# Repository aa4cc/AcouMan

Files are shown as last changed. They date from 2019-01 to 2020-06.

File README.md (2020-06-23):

# AcouMan - a platform for acoustic manipulation
[index](README.md)

# _!! IMPORTANT -- repository relocated !!_
Content in this repo is no longer updated.
Go to (https://gitlab.fel.cvut.cz/aa4cc/acouman/acouman-main) to get the latest version.
# _!! !!_

AcouMan is a platform for acoustic manipulation, that is for manipulating objects via shaping the surrounding acoustic pressure field. You can see the platform in the figure below and a detailed description will be (hopefully) published soon. If you want to see the platform in action, check our [video](https://youtu.be/BdDq_jRSNYA) showing some experiments with the platform.

This repository contains all files needed to reproduce the platform.

* [_MATLAB Optimization/_](MATLAB&#32;optimization/readme.md) folder contains Matlab scripts implementing a solver of the optimization problem where one looks for such phase shifts of the signals driving the transducer array that a given pressure point in space is generated
* [_FPGA generator/_](FPGA_generator/readme.md) folder contains a Quartus project for the 64 channel generator
* [_calibration/_](calibration/readme.md) folder contains all scripts for calibrating the camera
* [_manufacturing/_](manufacturing/readme.md) folder contains all drawings for a laser cutter, 3D models and PCB designs for manufacturing the platform
* [_simulink/_](simulink/readme.md) folder contains Simulink schemes for controlling the platform in various modes
* [_visualization/_](visualization/readme.md) folder contains Matlab scripts for visualization of the generated pressure field by the transducer array driven by square waves with specified phase-shifts
* [_webinterface/_](webinterface/readme.md) folder contains Python scripts for the web interface running on the Raspberry Pi

## Building the platform

If you want to build the platform, please refer to the guides on [mechanical assembly](docs/assembly.md) and [software](docs/software.md).

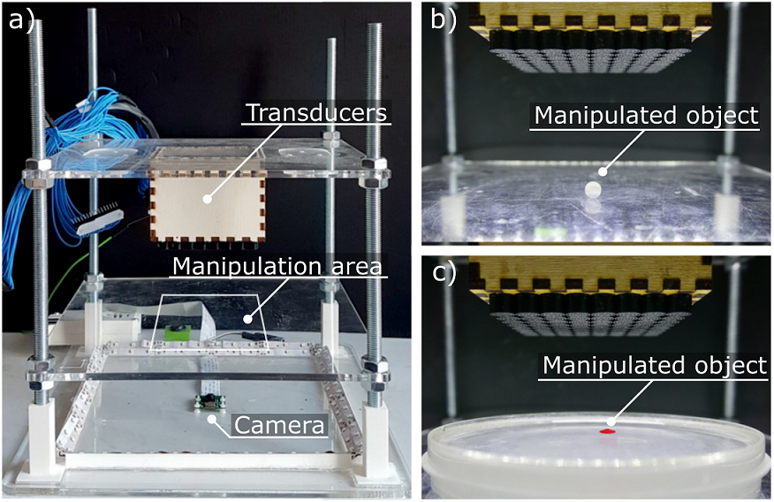
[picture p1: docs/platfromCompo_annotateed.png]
Photos of the platform


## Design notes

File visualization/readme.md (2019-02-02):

# Acoustic pressure field visualization tools
[index](../README.md) \> [visualization](readme.md)

Use the 'acousticPressureSlice' GUI to visualize the acoustic pressure field generated by the transducers. The GUI allows you to load the phase delays, either from the MATLAB workspace or a .mat file. You can set different slice planes (currently, only planes perpendicular to axes, ie. x = c, y = c or z = c, where c is an arbitrary constant, are supported). You can set the limits of the axes and resolution.

Alternatively, you can use the 'acousticPressure3D' function to calculate the pressure field, and then use function like 'slice' or 'isosurface' to visualize the field. To visualize the phase delays of the transducers, use the 'plotPhases' function.

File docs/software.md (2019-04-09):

# Building the platform - software
[index](../README.md) > [software](software.md)

For rapid prototyping, we use the following strategy:
We create our control scheme in MATLAB/Simulink and then deploy it to the Raspberry Pi.
The Raspberry then runs the control algorithm, which accepts the reference setpoints remotely via UDP.
This allows us to control the platform from a simple web interface.

## Configuring your PC

### Requirements

In order to deploy the controller to Raspberry Pi, you will need MATLAB & Simulink R2018b or newer _(note: we use this version of MATLAB, because it supports Raspberry Pi 3B+)_ with the following toolboxes/packages:
 * Simulink coder
 * Control systems toolbox
 * Simulink support package for Raspberry Pi

Also, your computer must have an SD card reader.

### Starting the Simulink models

If you change your working directory to _simulink_ and open any of the models, the startup functions should automatically add all necessary folders to MATLAB path.
If you encounter an error, try to run the scripts `BOD_startup` and `BOW_startup` manually.

## Configure the Raspberry Pi

### Install Raspbian with MATLAB server

Insert an empty microSD card in your computer.
In MATLAB, go to the _HOME_ card and select _Add-Ons-\>Manage Add-Ons_.
An Add-On Manager window should appear.

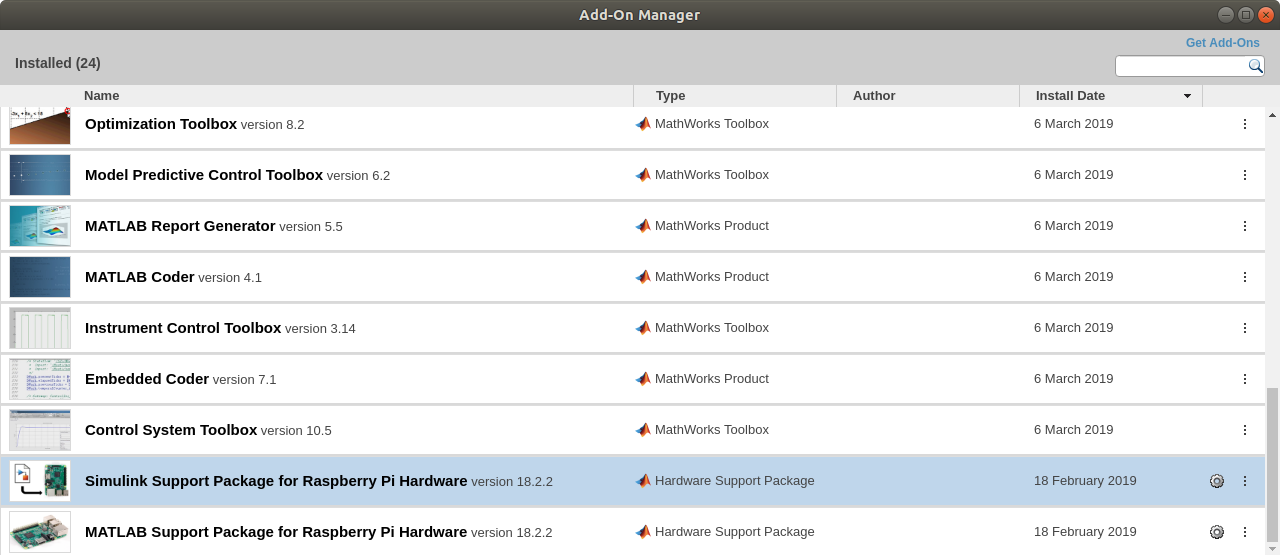
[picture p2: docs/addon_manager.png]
Add-On Manager


Find the Simulink Support Package and click on the Setup button (the gear).
Follow the guide and install the Raspbian image.

### Copy necessary files

From this repository, you will only need folders `raspi-ballpos` and `webinterface`.
On UNIX systems, use the following command to copy them from your computer:
```
scp -r raspi-ballpos/ webinterface/ pi@xxx.xxx.xxx.xxx:~
```

### Enable Camera

Either directly in the Raspberry Pi terminal, or remotely via SSH, type:
```
sudo raspi-config
```
and select the `Enable Camera` option.

### Install dependencies

#### OpenCV

Follow [this guide](https://www.pyimagesearch.com/2016/04/18/install-guide-raspberry-pi-3-raspbian-jessie-opencv-3/) on installing OpenCV on Raspbian Jessie.
_Note: The installation is quite lenghty. If you do it remotely, we recommend using `screen`, so you can disconnect without interrupting the process_

#### C++ libraries

Download [Eigen](http://eigen.tuxfamily.org/) and [LBFGS++](http://yixuan.cos.name/LBFGSpp/) libraries, and copy them to `/usr/include/`.

#### Python modules

Install the following modules using `pip`:
``` 
sudo pip3 install picamera click flask flask_socketio matplotlib profilehooks RPi.GPIO screeninfo imutils eventlet requests scipy
```
In addition, it may be necessary to upgrade the numpy module provided during OpenCV installation:
```
sudo pip3 install numpy --upgrade
```
Also, there are two custom packages in the `raspi-ballpos` folder that must be installed:
```
cd raspi-ballpos
cd sharemem/
sudo ./install
cd ../find_object/
sudo ./install
```

### Services

Copy all service files from `webinterface`:
```
sudo cp ~/webinterface/*.service /lib/systemd/system/
```
Enable the services at startup:
```
sudo systemctl enable posmeas.service 
sudo systemctl enable ultraman.service
sudo systemctl enable ultraman_web.service
```

### Configuration files

Move the configuration files from `webinterface` to user folder:
```
mv ~/webinterface/*.json ~/
```

## Deploy the controller

Open the Simulink model `simulink/allInOne.slx`.
Go to the _Model Parameters_ (the gear icon) and select _Hardware Implementation_.
Set _Hardware Board_ to Raspberry Pi, expand the _Target Hardware Resources_ tab and fill in the _Board Parameters_, as shown in the picture.

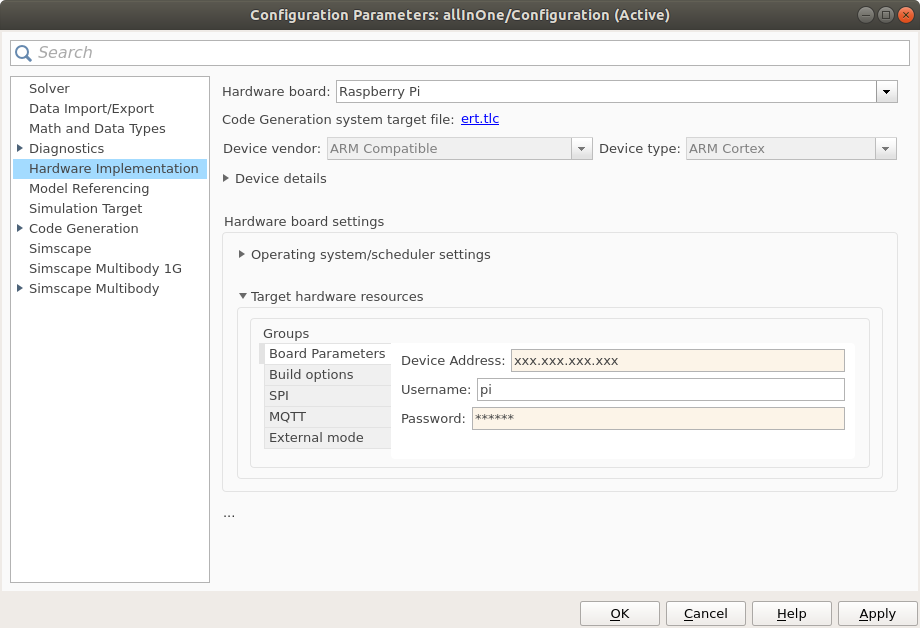
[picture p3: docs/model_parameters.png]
Model Parameters


Go to the _Build Options_ group and select _Build_ as the _Build Action_. Set the _Build Directory_ to `/home/pi`.

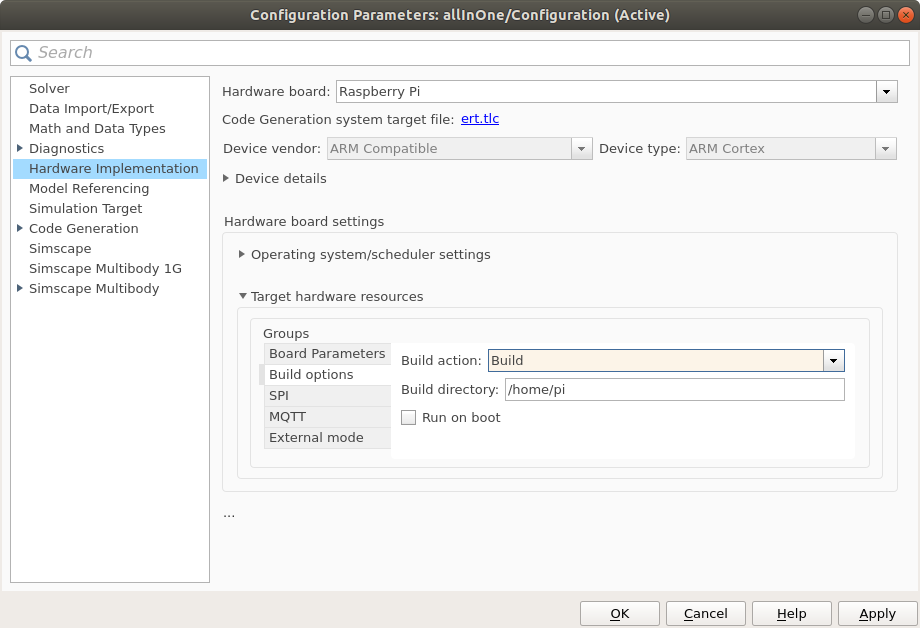
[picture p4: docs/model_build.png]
Model Parameters


Apply the changes and exit the _Model Parameters_ window.

Now, you can click on the _Deploy to Hardware_ button (the serial port icon).
If you cannot see the button, change the _Simulation Mode_ to _External_.

Since the R2018b version, MATLAB doesn't create the deployed model in the user folder.
You need to copy the controller:
```
cp ~/MATLAB_ws/R2018b/path_to_repository/simulink/allInOne.elf ~
```

## Controlling the platform

Now, you should be able to control the platform from the web interface.
Start the services so you don't need to restart the Raspberry.
```
sudo systemctl start posmeas.service 
sudo systemctl start ultraman.service
sudo systemctl start ultraman_web.service
```

On your computer, open a web browser.
The web interface should be accessible from port 5000 (`xxx.xxx.xxx.xxx:5000`).

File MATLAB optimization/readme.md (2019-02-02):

# MATLAB optimization scripts (deprecated)
[index](../README.md) \> [MATLAB optimization scripts](readme.md)

This document contains a brief introduction to the MATLAB optimization scripts. These scripts calculate phase delays for an array of 64 ultrasonic transducers. 

## Levitation

The 'levitation' folder contains scripts for single beam levitation method shown in an article by [Asier Marzo](https://www.nature.com/articles/ncomms9661). To generate the phase delays, run 'solverscript.m'. You must have the 'MATLAB optimization' folder in your MATLAB path to run this script. 

## Ghost Touch 

The 'ghostTouch' folder contains scripts for creating focused acoustic pressure, similarly to [Ghost Touch](http://doi.acm.org/10.1145/2817721.2817727). To generate the phase delays, use the function 'pressurePoints'. You must have the 'MATLAB optimization' folder in your MATLAB path to run this script.

__NOTE: All optimization scripts are now rewritten in C++ to be ran on the _Raspberry Pi_, the MATLAB scripts can still be used for verification.__

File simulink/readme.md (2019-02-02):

# Simulink models
[index](../README.md) \> [simulink](readme.md)

This document contains a description of the Simulink models and their usage.

## Simulink models

The models require the MATLAB system object from [raspi-ballpos](https://github.com/aa4cc/raspi-ballpos) to function. In addition, the compiler on the target device must have the [Eigen](http://eigen.tuxfamily.org/) and [LBFGS++](http://yixuan.cos.name/LBFGSpp/) libraries. All models are made to obtain reference or parameters via UDP. This can be done either using the simple MATLAB GUIs, or the Python [web interface](../webinterface/readme.md).

### All in one

This model implements all three models (bubbles, ball on solid surface, ball on water) with a switching system. It is created to be used with the [web interface](../webinterface/readme.md).

### Bubbles

This is a simple demonstration model. It creates a high-pressure point at a specified position.

### Ball on solid (dry) surface

This model implements a controller for positioning a ball on a dry surface. If the controller fails to stabilize the ball, check the calibration of the platform.

### Ball on water

This model implements a controller for positioning a floating ball. Ideally, the ball should be put in a transparent shallow container, such as a Petri dish, filled with water.

## GUIs 

The MATLAB GUIs are simple figures, set to appear on the secondary monitor. Check if the UDP port number in the .m files matches the UDP port number in the Simulink models.

All GUIs share similar controls. Dragging the circle changes position. In the 'bubbles' model, the mouse wheel changes the pressure intensity.

</html>

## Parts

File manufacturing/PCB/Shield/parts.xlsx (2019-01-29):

Parts needed for making 2 Shields
Farnell
Description | OC | Quantity | Unit price | Total
Cap. 1uF | 2494199 (https://cz.farnell.com/murata/gcm21br7ya105ka55l/cap-mlcc-x7r-1uf-35v-0805/dp/2494199) | 150 | 5.39 Kč | 808.95 Kč
Res. 0 Ohm | 2309112 (https://cz.farnell.com/multicomp/mc0805s8f0000t5e/res-thick-film-0r-1-0-125w-0805/dp/2309112) | 140 | 0.15 Kč | 20.86 Kč
Cap. 220uF | 2800123 (https://cz.farnell.com/teapo/ksh227m035s1g5h12k/cap-alu-elec-220uf-35v-rad/dp/2800123) | 6 | 3.31 Kč | 19.88 Kč
Cap. 100nF | 2896747 (https://cz.farnell.com/vishay/vj0805y104kxxac/cap-mlcc-x7r-0-1uf-25v-0805/dp/2896747) | 5 | 5.44 Kč | 27.22 Kč
Cap. 10nF | 2534062 (https://cz.farnell.com/wurth-elektronik/885012207066/cap-mlcc-x7r-0-01uf-25v-0805/dp/2534062) | 10 | 1.34 Kč | 13.38 Kč
Cap. 18pF | 2896683 (https://cz.farnell.com/vishay/vj0603a180jxbac/cap-mlcc-c0g-18pf-100v-0603/dp/2896683) | 10 | 3.67 Kč | 36.72 Kč
Cap. 4.7uF | 9451234 (https://cz.farnell.com/multicomp/mcgpr35v475m5x11/cap-alu-elec-4-7uf-35v-rad/dp/9451234) | 2 | 1.18 Kč | 2.36 Kč
Schottky | 2317416 (https://cz.farnell.com/on-semiconductor/nsr0320mw2t1g/diode-schottky-900ma-23v-sod-323/dp/2317416) | 5 | 5.01 Kč | 25.04 Kč
Polyfuse | 1861197 (https://cz.farnell.com/multicomp/mc36213/fuse-ptc-reset-smd-6v-500ma/dp/1861197) | 5 | 4.96 Kč | 24.78 Kč
Ferrite bead | 1301674 (https://cz.farnell.com/tdk/mmz2012y152b/ferrite-bead-0-4ohm-500ma-0805/dp/1301674) | 10 | 1.76 Kč | 17.64 Kč
LED - amber | 2251467 (https://cz.farnell.com/vishay/vlmk233u1aa-gs08/led-mini-amber-power/dp/2251467) | 5 | 2.75 Kč | 13.74 Kč
LED - yellow | 2099250 (https://cz.farnell.com/kingbright/kpt-3216yc/led-1206-yellow-8mcd-588nm/dp/2099250) | 5 | 1.42 Kč | 7.12 Kč
Crystal | 2508453 (https://cz.farnell.com/qantek-technology-corporation/qcl12-0000f18b23b/crystal-12mhz-18pf-hc-49us/dp/2508453) | 2 | 4.65 Kč | 9.30 Kč
Res. 510 kOhm | 2447678 (http://cz.farnell.com/multicomp/mcwr08x5103ftl/res-thick-film-510kohm-1-0-125w/dp/2447678) | 10 | 0.25 Kč | 2.47 Kč
Res. 2.1 Mohm | 2139153 (https://cz.farnell.com/vishay/crcw08052m10fkea/res-thick-film-2m1-1-0-125w-0805/dp/2139153) | 10 | 0.43 Kč | 4.29 Kč
Res. 169 kOhm | 2695000 (https://cz.farnell.com/multicomp/mcwr08x1693ftl/res-thick-film-169k-1-0-125w-0805/dp/2695000) | 10 | 0.25 Kč | 2.47 Kč
Res. 58 kOhm | 2694636 (https://cz.farnell.com/multicomp/mcwr04x5762ftl/res-thick-film-57k6-1-0-0625w/dp/2694636) | 10 | 0.12 Kč | 1.16 Kč
Res. 50 Ohm | 2059274 (https://cz.farnell.com/panasonic-electronic-components/erj3ekf49r9v/res-thick-film-49r9-1-0-1w-0603/dp/2059274) | 10 | 1.06 Kč | 10.63 Kč
Res. 65 Ohm | 2303421 (https://cz.farnell.com/panasonic-electronic-components/erj6enf66r5v/res-thick-film-66r5-1-0-125w-0805/dp/2303421) | 10 | 0.61 Kč | 6.06 Kč
MOSFET | 2777608 (http://cz.farnell.com/nexperia/phkd3nq10t-518/mosfet-dual-n-ch-100v-3a-soic/dp/2777608) | 5 | 12.76 Kč | 63.81 Kč
UCC27531 | 2307940 (https://cz.farnell.com/texas-instruments/ucc27531dbvt/gate-driver-35v-2-5-5a-assym-6sot23/dp/2307940) | 140 | 37.24 Kč | 5213.04 Kč
FT232R | 1146032 (http://cz.farnell.com/ftdi/ft232rl-reel/ic-usb-to-uart-smd-28ssop/dp/1146032) | 4 | 96.56 Kč | 386.23 Kč
MINI USB | 1125348 (http://cz.farnell.com/molex/67503-1020/mini-usb-2-0-otg-type-b-rcpt-smt/dp/1125348) | 3 | 13.53 Kč | 40.60 Kč
BNC Jack | 1020955 (https://cz.farnell.com/greenpar-te-connectivity/1-1337543-0/rf-coaxial-bnc-right-angle-jack/dp/1020955) | 2 | 29.02 Kč | 58.04 Kč
 |  |  |  | 6815.78 Kč
Mouser
Description | OC | Quantity | Unit price | Total
LTC4365 | 584-C4365ITS8TRMPBF (https://cz.mouser.com/ProductDetail/Analog-Devices/LTC4365ITS8TRMPBF) | 2 | 90.74 Kč | 181.48 Kč

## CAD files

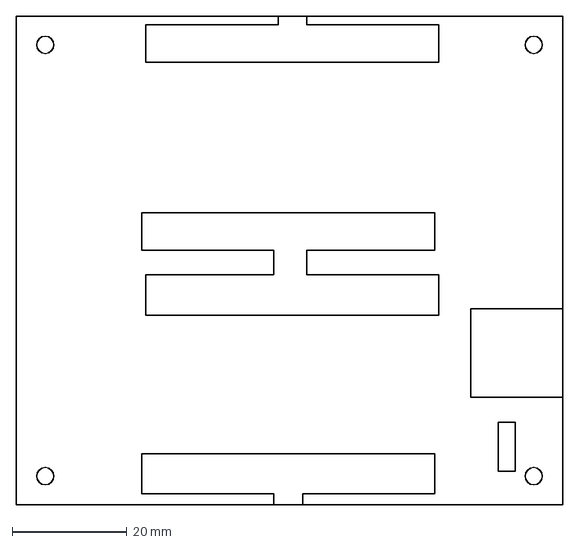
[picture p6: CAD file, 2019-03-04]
manufacturing/laser cut/shield.dxf
95.0 x 85.0 mm

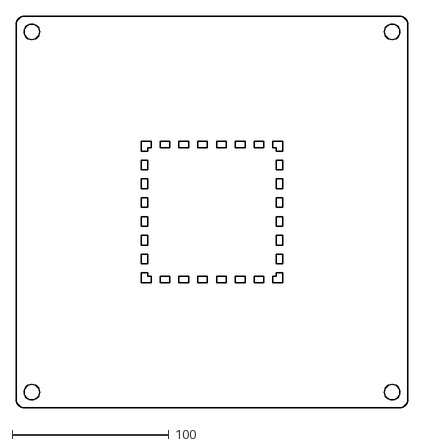
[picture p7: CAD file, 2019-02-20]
manufacturing/laser cut/upperPanel.dxf
250.0 x 250.0

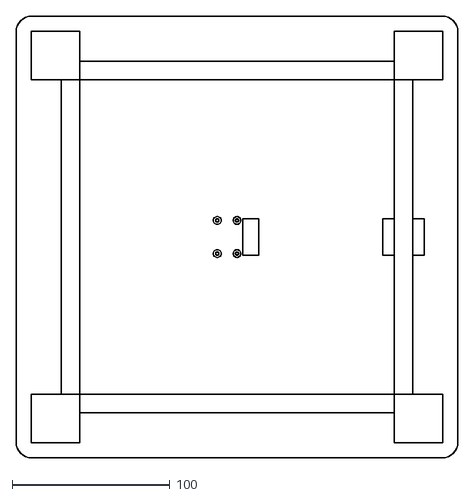
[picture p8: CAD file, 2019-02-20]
manufacturing/laser cut/bottomPanel.dxf
280.0 x 280.0

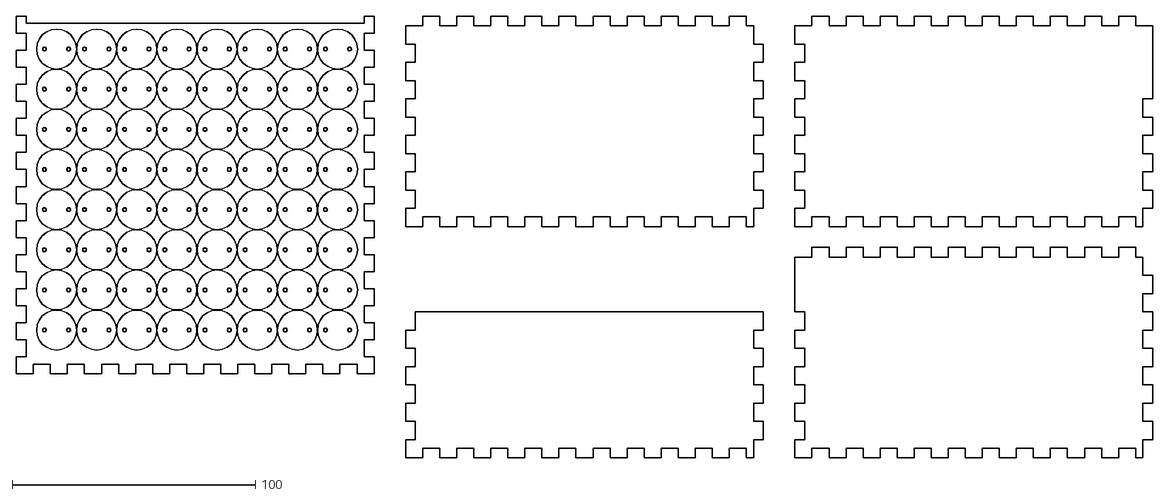
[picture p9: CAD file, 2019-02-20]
manufacturing/laser cut/bigTransducerBox.dxf
467.0 x 181.5

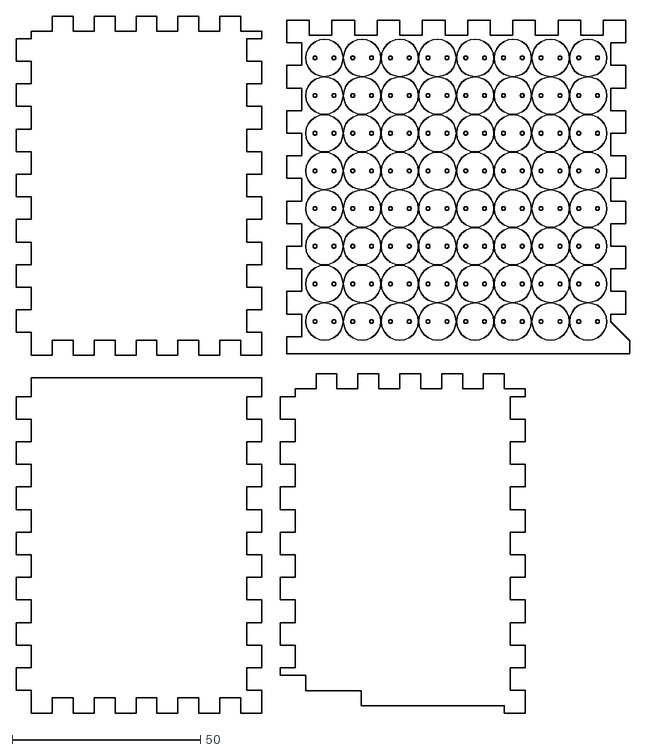
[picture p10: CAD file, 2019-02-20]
manufacturing/laser cut/transducerBox.dxf
162.8 x 185.0

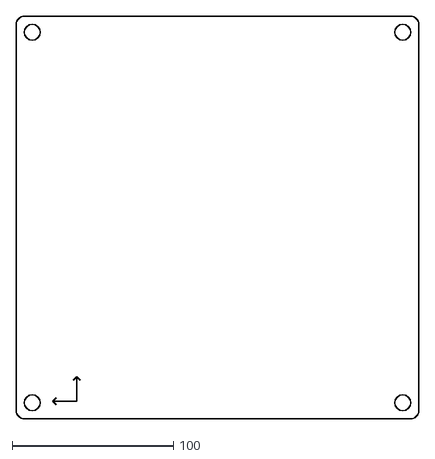
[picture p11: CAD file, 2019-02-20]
manufacturing/laser cut/middlePanel.dxf
249.7 x 249.7

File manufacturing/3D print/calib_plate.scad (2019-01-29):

$fn=100;

// cuts out small holes at the centers
// of transducers if enabled
holes = 0;

difference() {
    union() {
        translate([12.5,12.5,1])
            cube([85,85,3]);
        cube([110,110,1]);
    }
    union() {
        for (i=[0:7]) {
           translate([20+i*10,20,1])
             cylinder(d=10.25,h=3);
           translate([20+i*10,90,1])
             cylinder(d=10.25,h=3);
           translate([20,20+i*10,1])
             cylinder(d=10.25,h=3);
           translate([90,20+i*10,1])
             cylinder(d=10.25,h=3);
        }
        if (holes) {
            for (i=[0:7]) {
                for (j=[0:7]) {
                    translate([20+i*10,20+j*10,0])
                        cylinder(d=2,h=0.6);
                }
            }
        }
        translate([20,20,1])
            cube([70,70,3]);
    }
}

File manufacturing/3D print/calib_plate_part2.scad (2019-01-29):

$fn=100;

for (i=[0:7]) {
    for (j=[0:7]) {
        translate([15+i*10,15+j*10,0])
            cylinder(d=2,h=0.6);
    }
}

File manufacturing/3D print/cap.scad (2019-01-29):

hole_drill = 9;
hole_depth = 5;
cap_diam = 15;
cap_height = 20;

$fn = 100;

difference() {
    union() {
        cylinder(d = cap_diam,h = cap_height-cap_diam);
        translate([0,0,cap_height-cap_diam])
            intersection() {
                sphere(d = cap_diam);
                cylinder(d = cap_diam,h = cap_diam);
            }
    }
    cylinder(d = hole_drill, h = hole_depth);
}

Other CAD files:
manufacturing/3D print/PFL34_lock.scad
manufacturing/3D print/pillar.scad
manufacturing/3D print/prism.scad
manufacturing/3D print/triangle.scad

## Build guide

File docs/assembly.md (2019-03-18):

# Building the platform

[index](../README.md) > [assembly](assembly.md)

This documents describes what [components](#required-components) you need and how to [assemble](#assembly) them. Once you finish mechanical assembly, check the guide on [software](software.md).

## Required components

All source files required for building the platform are located in the [manufacturing](../manufacturing/readme.md) folder.

### Laser-cut components

The drawings are located in `manufacturing/laser cut` folder in DXF format, and can be opened, for instance, with LibreCAD. Set the units to millimeters. The drawings are split into layers named _Cut_ and _Engrave_ (or, in complicated cases _EngraveTop_ and _EngraveBottom_). Shapes in _Engrave_ layers should be filled (you need to engrave the whole shape, not just its outline).

You need to laser cut the following drawings: _top_, _middle_ and _bottom panel_, and _small transducer box_. The panels must be made from transparent and sturdy material, we recommend using 5mm thick plexiglass. The features engraved in the _bottom panel_ need to be about 1.5-2 mm deep. The _small transducer box_ is designed to be cut from 4mm thick material, we recommend using plywood.

Optionally, you can cut-out the _shield_ from plexiglass.

### 3D printed components

The models are located in `manufacturing/3D print` in SCAD format. You need to print four copies of models named _pillar_ and _prism_. We recommend printing from PLA on fast or better quality. Optionally, you can also print four protective _caps_ from a soft, flexible material like PLA FLEX or TPU.

### PCB

The PCBs are created in Eagle and use custom libraries, located in the project folder. You need two PCBs, _shield_ and _small transducer board_. All PCB components are listed in the bill of material (BOM - for [shield](../manufacturing/PCB/Shield/BOM.html) and [transducer board](../manufacturing/PCB/TransducerBoard/BOM.html)). In addition, you will also need 34 core flat cable and connectors, that mate with the pin headers on the PCBs.

Description of all necessary signal connectors and their illustration photos are shown in the picture below. ___NOTE:___ _Since we were unable to find 32 core flat cable with connectors, we are using 34 core cable with 2x17 connectors_

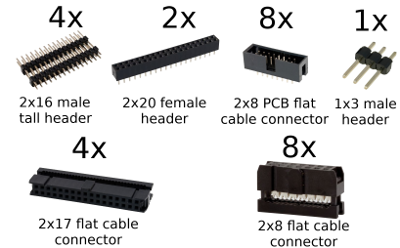
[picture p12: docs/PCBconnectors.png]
All necessary signal connectors


### Additional hardware

Apart from the aforementioned components, you will also need:

 * Raspberry Pi model B or B+
 * Raspberry Pi camera module v1.3
 * Terasic DE0 Nano
 * Power supply capable of providing 16V-18V @ 1A
 * 2 meters (8x25 cm segments) of LED stripes and a source to power them
 * 1.2 meters (4x30 cm segments) of M10 threaded rod
 * 8x M10 nuts
 * 4x M2 screws and nuts
 * if you decided to cut-out the plexiglass shield, you will also need 8x M3 screws and 4x M3x12 standoffs (both sides female)

## Assembly

### Determine the polarity of transducers

To do this, you will need a function generator and a two-channel oscilloscope. Set the function generator to 40 kHz 5 Vpp sine wave, and connect its output to one transducer (we will call it the reference transducer) and to the first channel of the oscilloscope. Then, connect another transducer (we will call it the test transducer) to the second channel of the oscilloscope and bring the two transducers close.

On the oscilloscope, you should see a sine wave that is (almost) in phase, or out of phase with the signal coming from the generator (see image below). Based on the measurement, mark the contact on the test transducer, which is connected either to the probe live or ground. Repeat the process for all 64 transducers.

How to determine the polarity of transducers

### Assemble the transducer box

 1. Align the top of the laser-cut transducer box with the transducer board PCB (as shown in image below). 
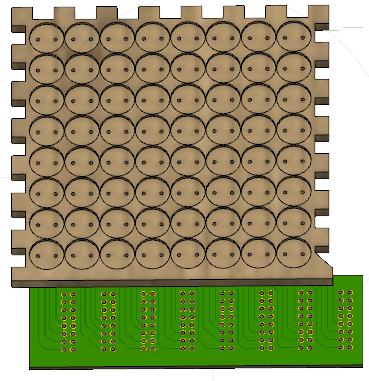
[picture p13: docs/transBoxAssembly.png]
Align transducer box with PCB
 
 2. Slide the transducers into the engraved slots (mind the polarity) and solder them to the PCB.
 3. Solder the 2x8 flat cable connectors. The orientation of the connectors is shown in the image below.
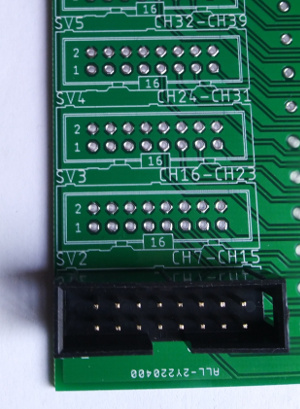
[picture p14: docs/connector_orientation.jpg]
2x8 connector orientation
 
 4. Take the remaining parts of the transducer box, put glue on the finger joints, and assemble the box.

### Assemble the platform

#### Start with the bottom panel.
 1. Slide four M2 screws through the laser-cut holes in the center from below, slide the camera module on the screws and fasten it in place with the nuts. 
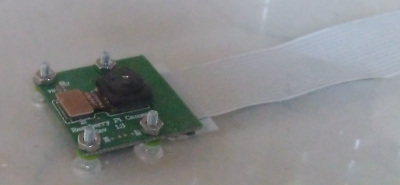
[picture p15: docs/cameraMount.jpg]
Camera mount
 
 2. Use an M10 screw tap to drill thread in the 3D printed pillars.
 3. Attach the pillars and prisms to the engraved slots of the bottom panel with glue. Do not use hot glue, it doesn't stick to plexi, use special glue for plastics. The ribbon cable of the camera module must lead under one of the prisms.
 4. Create a chain of LED stripe segments by soldering wires to their contacts (use about 2 - 3 cm long wires) with one end connected to the LED power supply.
 5. Glue the LED stripes to the prisms, you should be able to fit two segments on each.

#### Now, we can add the middle panel.
 1. Screw one M10 nut on each of the four threaded rods, about 10 cm in.
 2. Screw the threaded rods into the pillars (as far as they will go). You could do steps 1 and 2 the other way around, but this will save you some tedious screwing.
 3. Slide on the middle panel. The panel should be oriented so, that if the ribbon cable of the camera is pointing upwards, the _x,y_ axis description should be in the bottom left corner (see the picture below). 
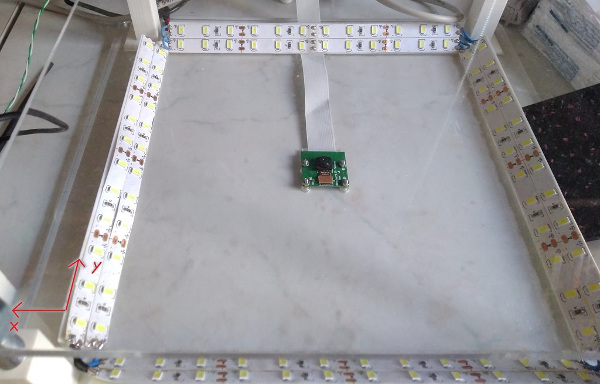
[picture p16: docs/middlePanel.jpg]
Middle panel orientation
 
 4. Using a tape measure and spirit level, adjust the nuts, so that the middle panel sits about 8 cm above the bottom panel and is level.
 5. Screw in four more nuts to fixate the middle panel both from top and bottom.

#### Finally, we can put together the top panel and complete the platform.
 1. Slide the finger joints of the transducer box into the top panel and glue both parts together.
 2. Screw in four more nuts, this time about 15 cm above the middle panel.
 3. Slide on the top panel with transducers. The PCB connectors should point in the same direction as the ribbon cable of the camera.
 4. Adjust the nuts, so that the distance between the middle panel and the transducers is 65 mm.
 5. Screw in four more nuts to fixate the top panel both from top and bottom.

### Build the shield

#### Program the FPGA

Before building the shield, you need to change the programming of the DE0-Nano board. The Quartus project is located in the _FPGA generator_ folder. For information on how to program the permanent memory of the device, please refer to the user manual available on [Terasic website](https://www.terasic.com.tw/cgi-bin/page/archive.pl?Language=English&CategoryNo=139&No=593&PartNo=4), chapter 9.1.

_Note: Programming the permanent memory takes effect after restarting the device (i.e. disconnecting power supply)._ 

#### Solder the shield PCB

This is relatively straightforward, but time consuming. Make sure to solder all ICs the correct way. If you have the laser-cut plexiglass shield, you can mount it on top of the PCB using the M3 screws and spacers.

#### Connect the shield with the FPGA

You must remove the plexiglass from the FPGA board in order to connect the boards. You may also have to unsolder/cut off this two-pin header from the FPGA.

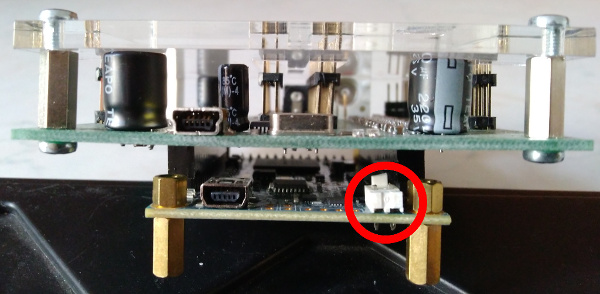
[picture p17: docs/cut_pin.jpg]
Cut off pin header


Now, just slide the two boards into each other, but mind the orientation. The silkscreens of both boards should be oriented the same way. Also, the miniUSB connectors on both boards should be on the same side.

### Cables and testing

As mentioned above, we use 34 core flat cable. On one end of the cable, we have a 2x17 connector. The other end is split into 16, 16 and 2 unused cores with two 2x8 connectors. Make four cable with the connectors, as shown in the picture below.

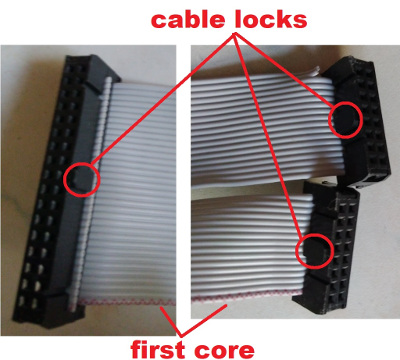
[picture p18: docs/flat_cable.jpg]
Flat cable


If you want to check, that your assembled generator is working, you can run the `generatorCommDemo.py` script located in `simulink/system_object/newGenerator/`. Just connect both miniUSB cables to your PC and change the default 'COM5' port in the script for the port of the USB-UART converter found in the device manager. On pressing Enter, the script should individually turn on all channels.

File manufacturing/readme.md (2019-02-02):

# Manufacturing
[index](../README.md) \> [manufacturing](readme.md)

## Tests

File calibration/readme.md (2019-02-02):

# MATLAB calibration scripts (deprecated)
[index](../README.md) \> [calibration](readme.md)

The calibration calculates the rotaion matrix used by the coordinate transform scripts.
In 'calibrate_8x8', mark the centers of all transducers.
In 'calibrate_4x4', mark only the 16 transducers in the middle.

__NOTE: Since the integration of the calibration scripts in [web interface](../webinterface/readme.md), the MATLAB calibration scripts are no longer used.__

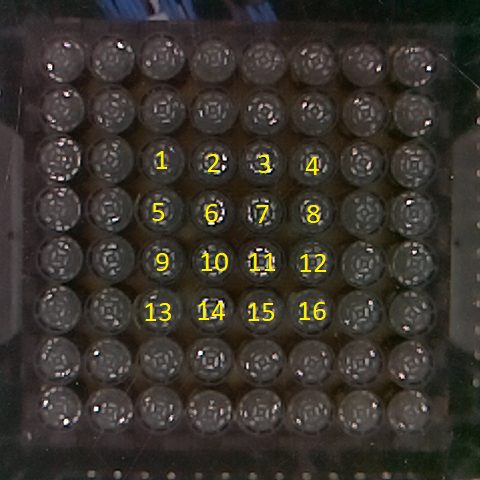
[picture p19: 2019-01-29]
calibration/caliborder_4x4.png

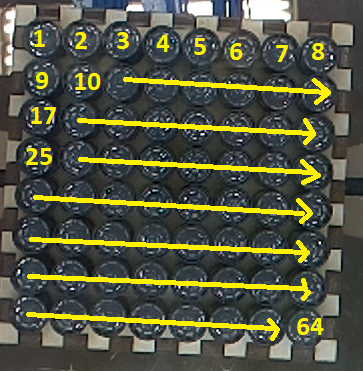
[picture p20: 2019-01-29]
calibration/caliborder_8x8.png

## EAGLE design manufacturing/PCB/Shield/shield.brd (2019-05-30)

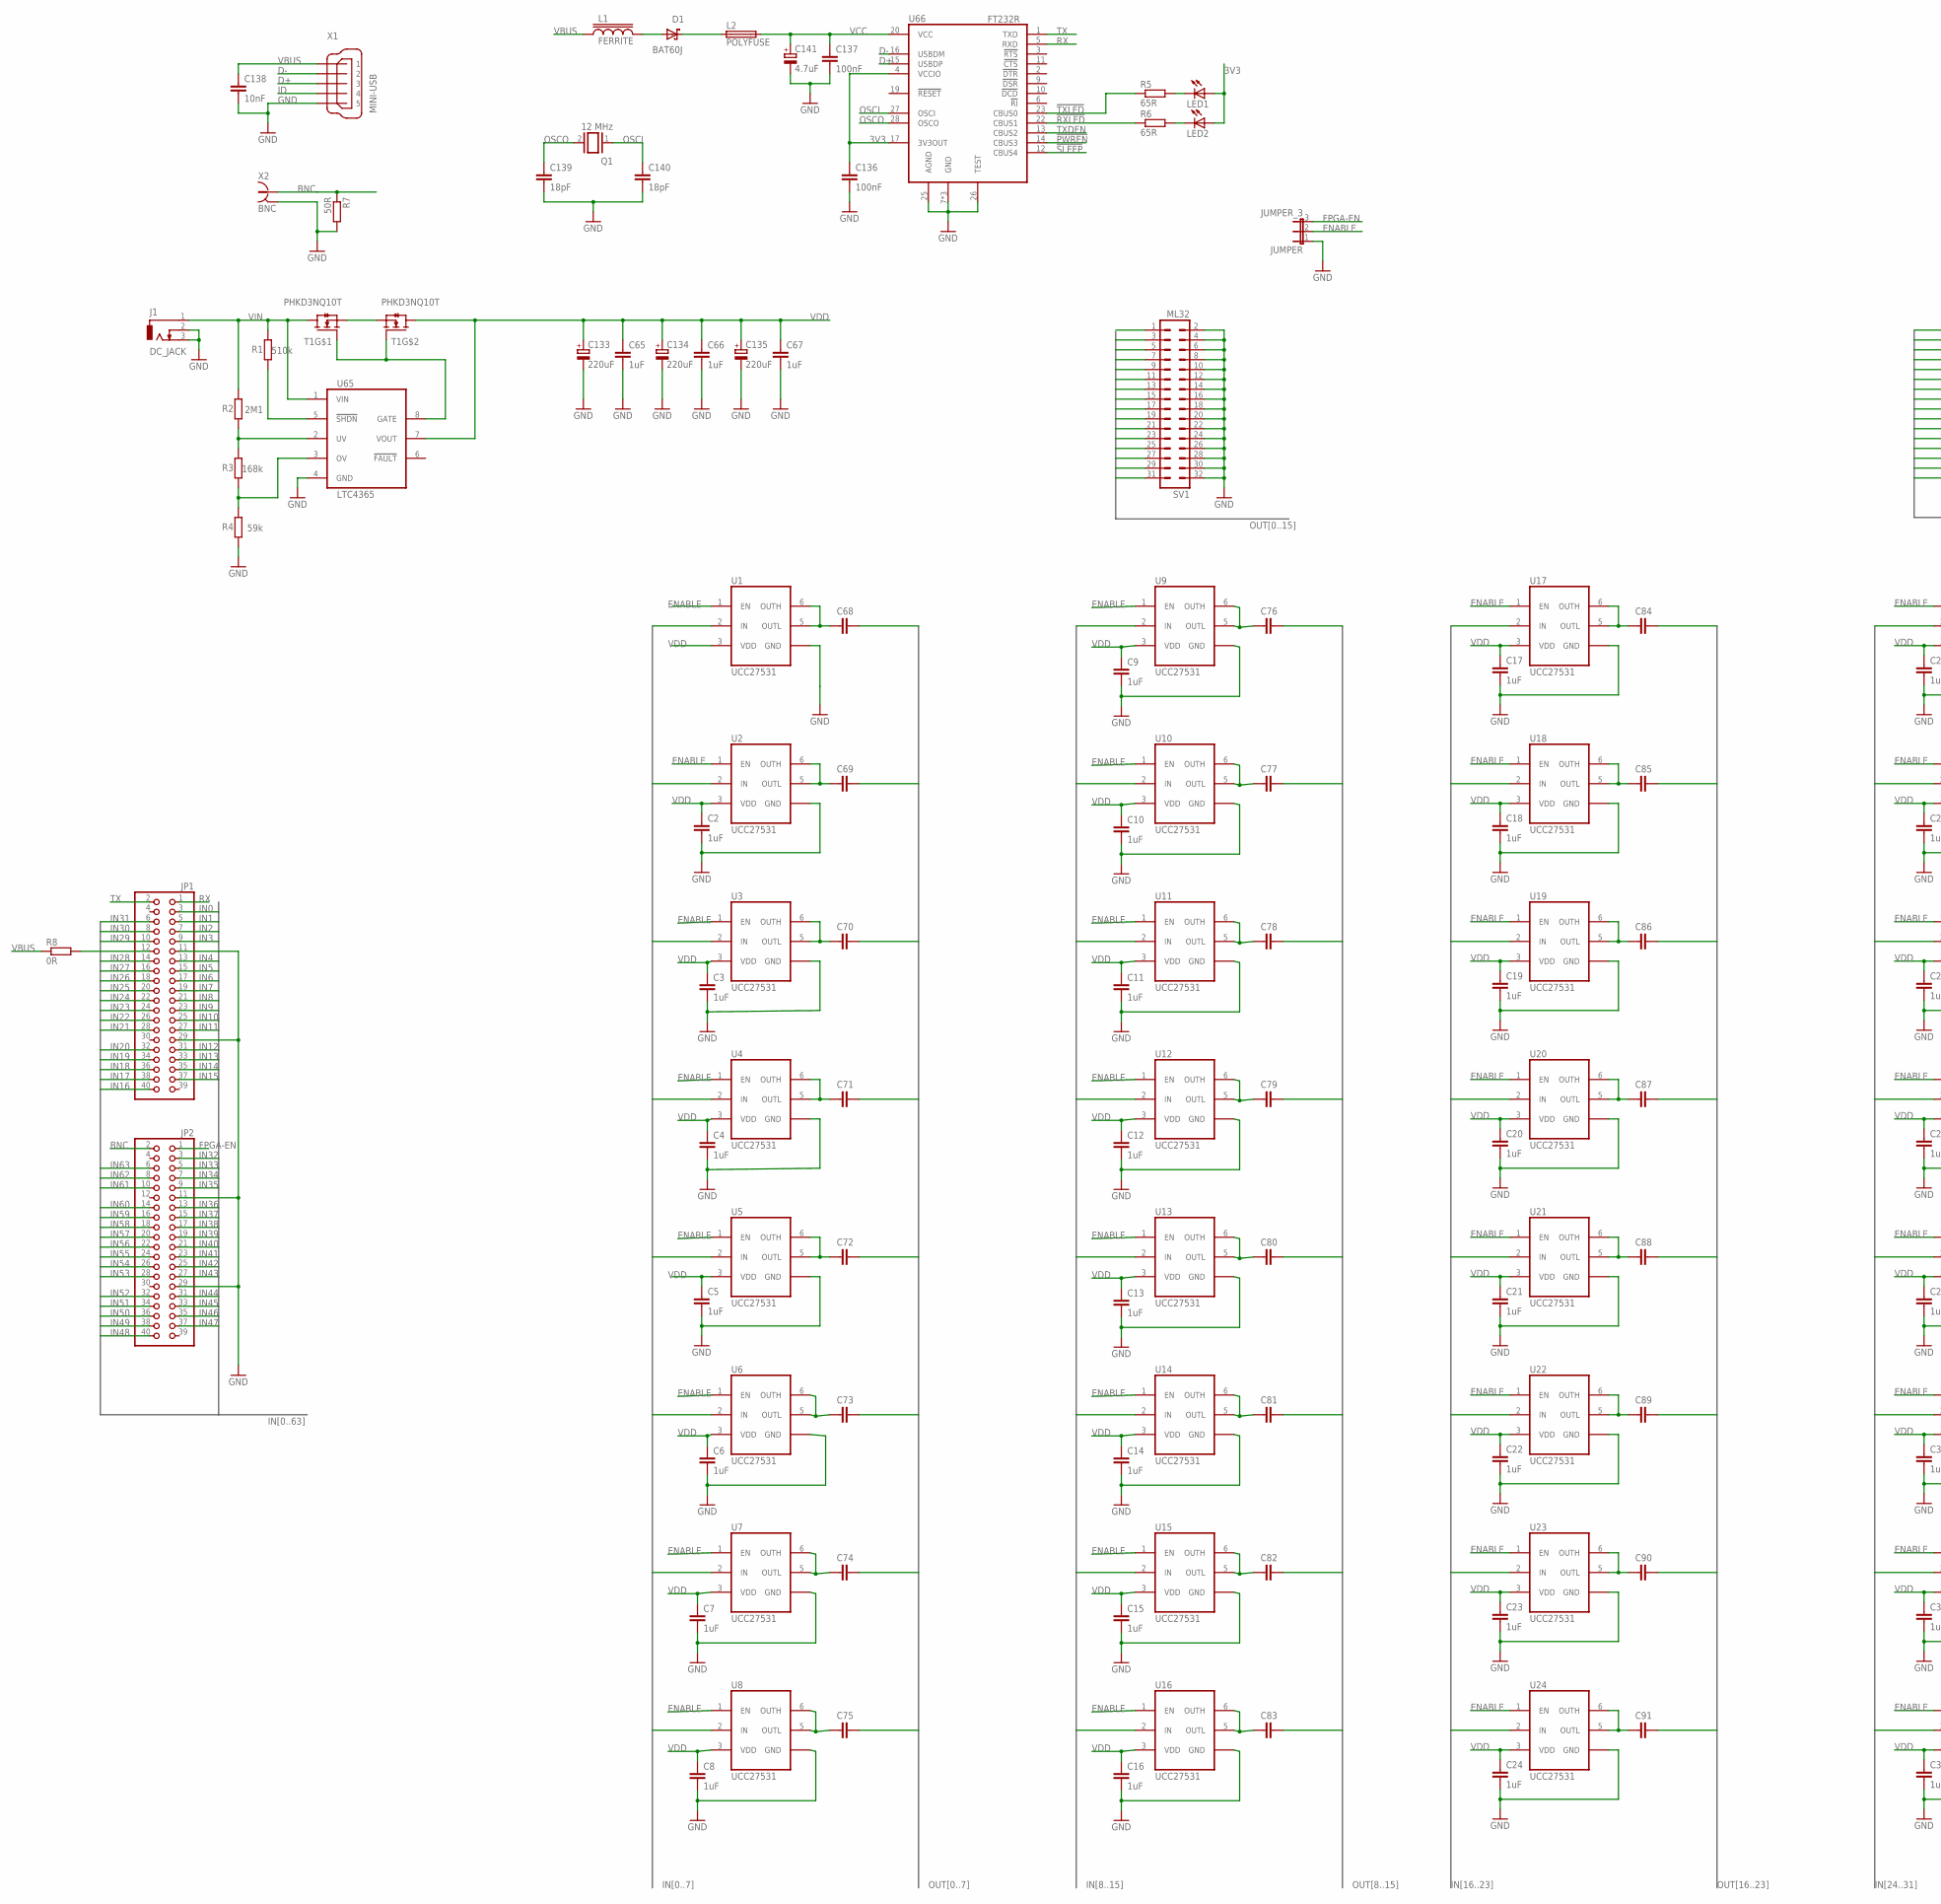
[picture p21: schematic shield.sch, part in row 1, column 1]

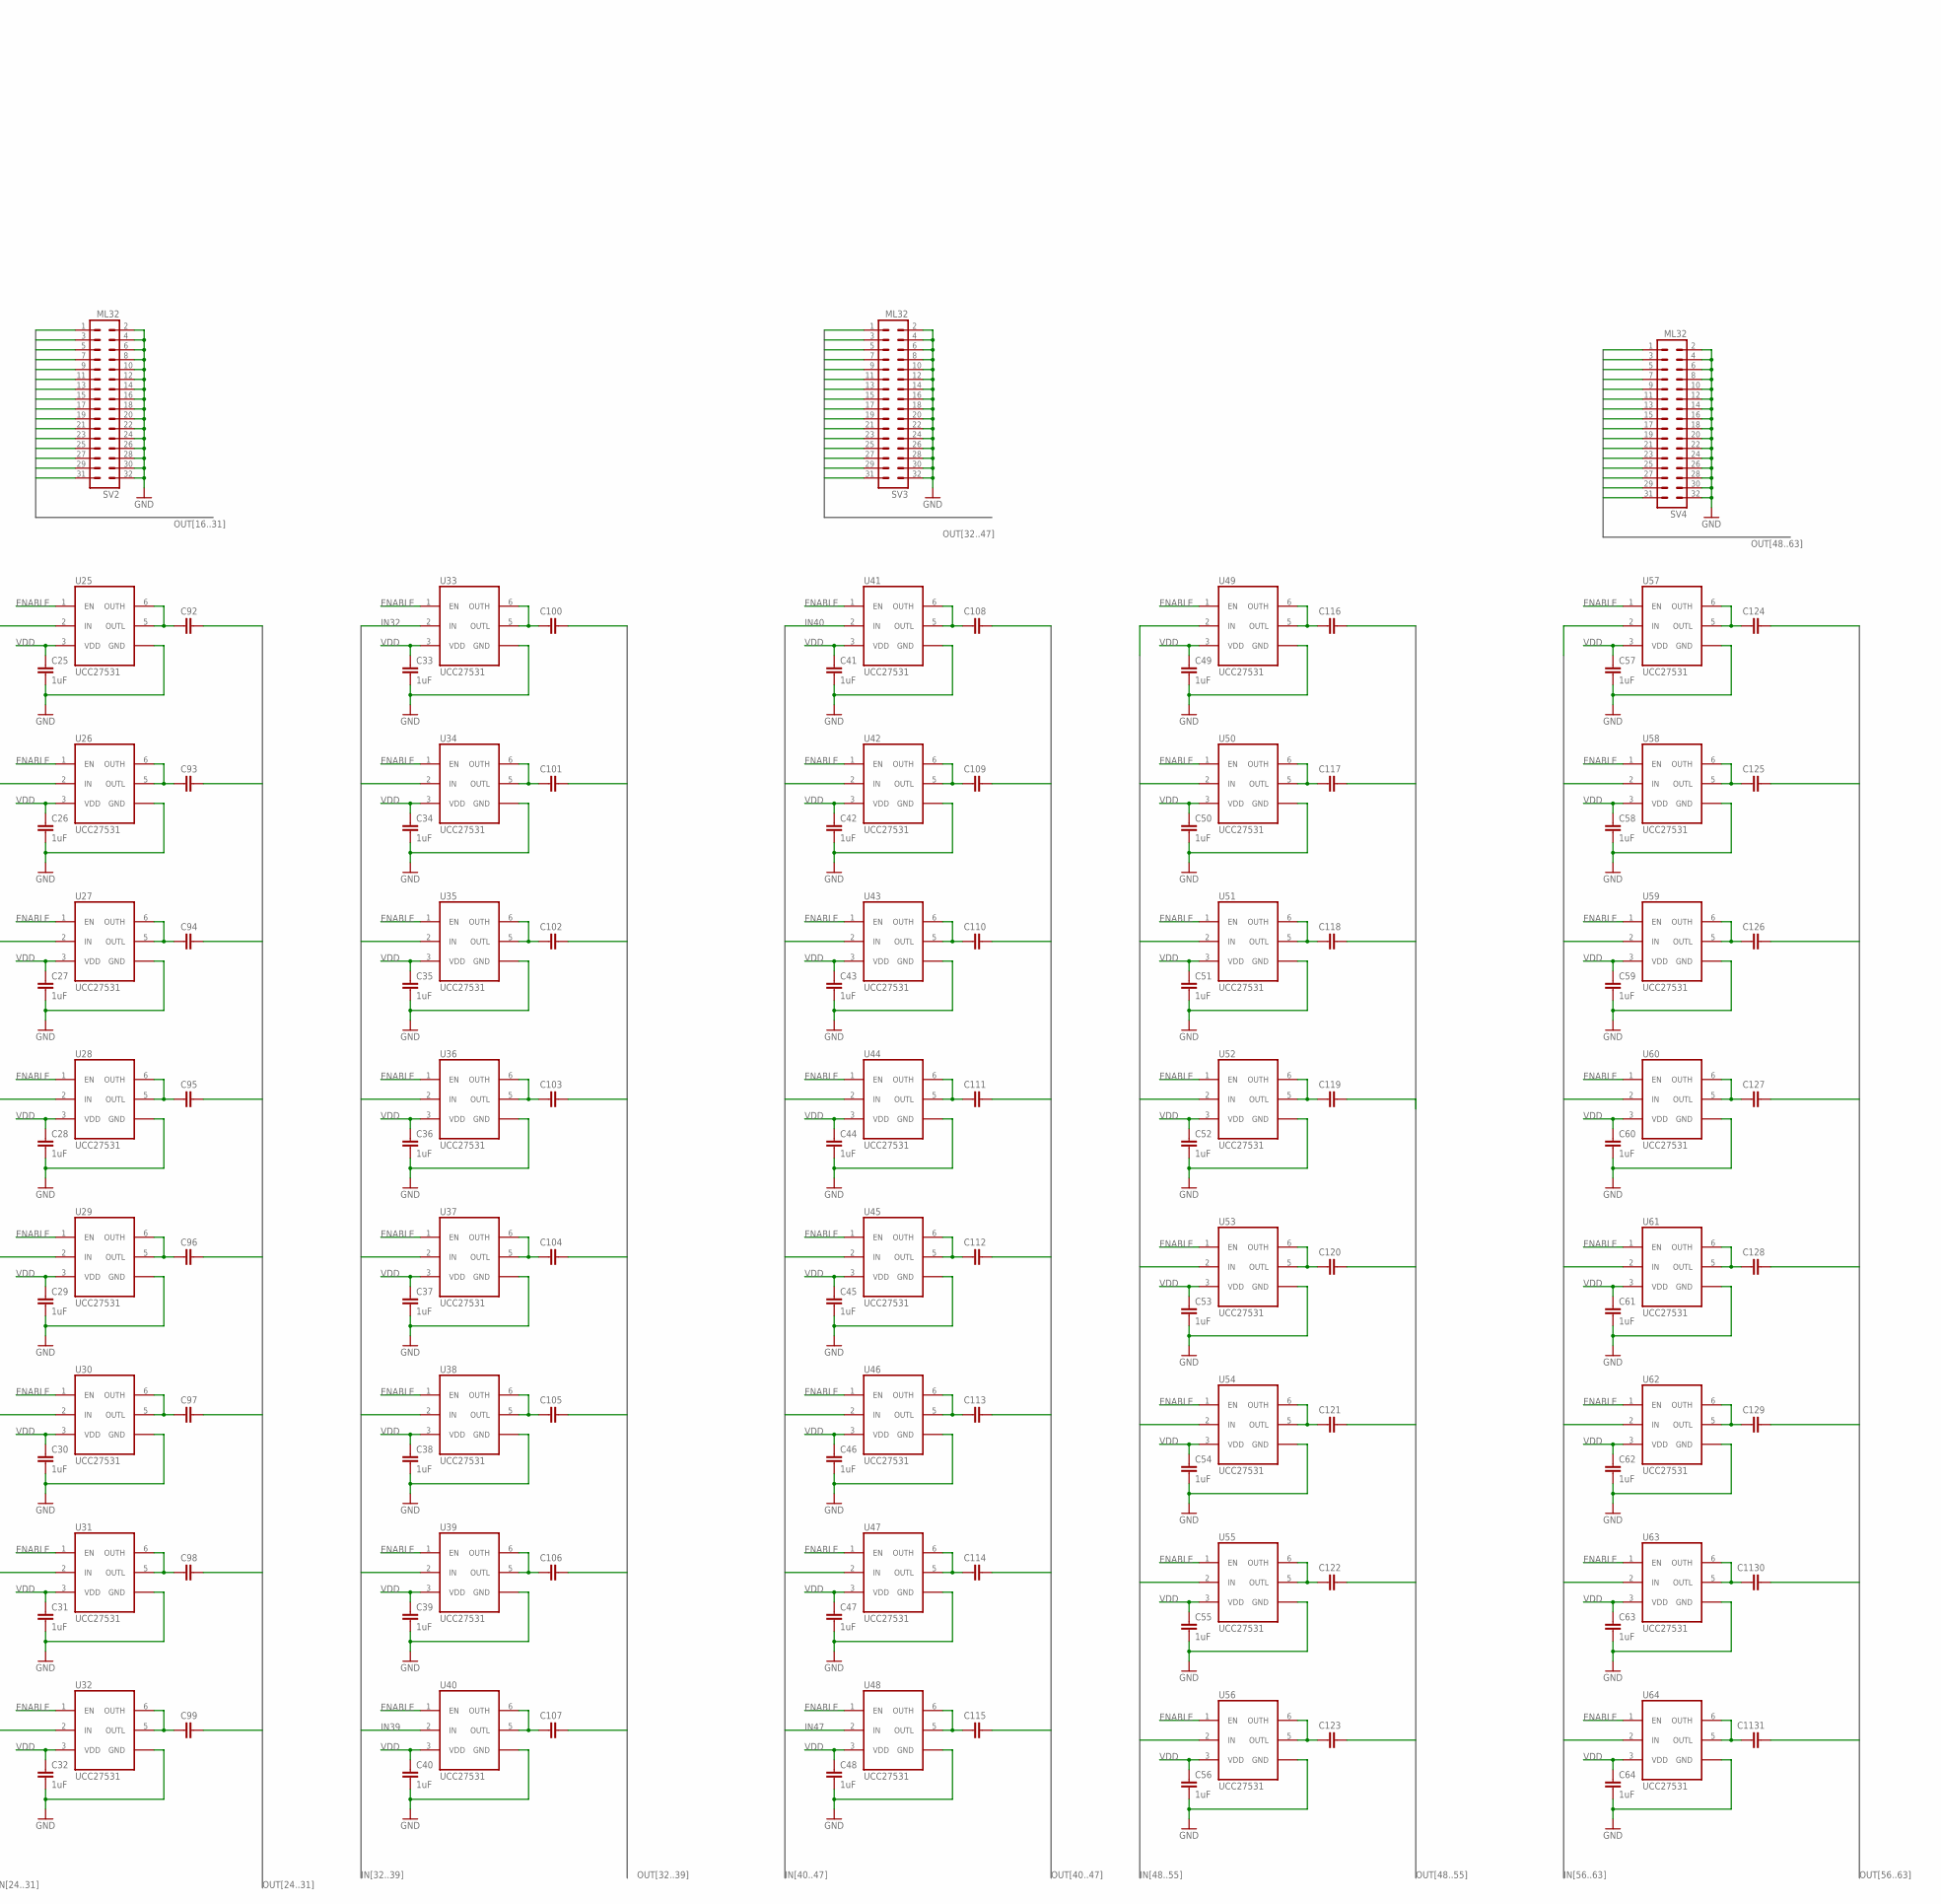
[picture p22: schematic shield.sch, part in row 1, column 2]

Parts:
C2, C3, C4, C5, C6, C7, C8, C9, C10, C11, C12, C13, C14, C15, C16, C17, C18, C19, C20, C21, C22, C23, C24, C25, C26, C27, C28, C29, C30, C31, C32, C33, C34, C35, C36, C37, C38, C39, C40, C41, C42, C43, C44, C45, C46, C47, C48, C49, C50, C51, C52, C53, C54, C55, C56, C57, C58, C59, C60, C61, C62, C63, C64, C65, C66, C67: 1uF; C0805
C68, C69, C70, C71, C72, C73, C74, C75, C76, C77, C78, C79, C80, C81, C82, C83, C84, C85, C86, C87, C88, C89, C90, C91, C92, C93, C94, C95, C96, C97, C98, C99, C100, C101, C102, C103, C104, C105, C106, C107, C108, C109, C110, C111, C112, C113, C114, C115, C116, C117, C118, C119, C120, C121, C122, C123, C124, C125, C126, C127, C128, C129, C1130, C1131: C; C0805
C133, C134, C135: 220uF; E5-10,5
C136, C137: 100nF; C0805
C138: 10nF; C0805
C139, C140: 18pF; C0603
C141: 4.7uF; E2-5
D1: BAT60J; SOD323_ST
J1: DC_JACK; DCJ0202
JP1, JP2: PINHD-2X20; 2X20
JUMPER: JUMPER_3; JP2
L1: FERRITE; SML0805
L2: POLYFUSE; SML0805
LED1, LED2: LEDSML1206; SML1206
Q1: 12 MHz; QS
R1: 510k; R0805
R2: 2M1; R0805
R3: 168k; R0805
R4: 59k; R0805
R5, R6: 65R; R0805
R7: 50R; R0603
R8: 0R; R0805
SV1, SV2, SV3, SV4: ML32
T1: PHKD3NQ10T; SO8
U1, U2, U3, U4, U5, U6, U7, U8, U9, U10, U11, U12, U13, U14, U15, U16, U17, U18, U19, U20, U21, U22, U23, U24, U25, U26, U27, U28, U29, U30, U31, U32, U33, U34, U35, U36, U37, U38, U39, U40, U41, U42, U43, U44, U45, U46, U47, U48, U49, U50, U51, U52, U53, U54, U55, U56, U57, U58, U59, U60, U61, U62, U63, U64: UCC27531; DBV_R-PDSO-G6
U65: LTC4365; TSOT23-8
U66: FT232R; SSOP28
X1: MINI-USB; 32005-201
X2: BNC; BNC_CUSTOM

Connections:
3V3: C136.1, LED1.A, LED2.A, U66.4 (VCCIO), U66.17 (3V3OUT)
!PWREN!: U66.14 (CBUS3)
!RXLED!: R6.1, U66.22 (CBUS1)
!SLEEP!: U66.12 (CBUS4)
!TXLED!: R5.1, U66.23 (CBUS0)
BNC: JP2.2, R7.1, X2.1
D+: U66.15 (USBDP), X1.3
D-: U66.16 (USBDM), X1.2
ENABLE: JUMPER.2, U1.1 (EN), U2.1 (EN), U3.1 (EN), U4.1 (EN), U5.1 (EN), U6.1 (EN), U7.1 (EN), U8.1 (EN), U9.1 (EN), U10.1 (EN), U11.1 (EN), U12.1 (EN), U13.1 (EN), U14.1 (EN), U15.1 (EN), U16.1 (EN), U17.1 (EN), U18.1 (EN), U19.1 (EN), U20.1 (EN), U21.1 (EN), U22.1 (EN), U23.1 (EN), U24.1 (EN), U25.1 (EN), U26.1 (EN), U27.1 (EN), U28.1 (EN), U29.1 (EN), U30.1 (EN), U31.1 (EN), U32.1 (EN), U33.1 (EN), U34.1 (EN), U35.1 (EN), U36.1 (EN), U37.1 (EN), U38.1 (EN), U39.1 (EN), U40.1 (EN), U41.1 (EN), U42.1 (EN), U43.1 (EN), U44.1 (EN), U45.1 (EN), U46.1 (EN), U47.1 (EN), U48.1 (EN), U49.1 (EN), U50.1 (EN), U51.1 (EN), U52.1 (EN), U53.1 (EN), U54.1 (EN), U55.1 (EN), U56.1 (EN), U57.1 (EN), U58.1 (EN), U59.1 (EN), U60.1 (EN), U61.1 (EN), U62.1 (EN), U63.1 (EN), U64.1 (EN)
FPGA-EN: JP2.1, JUMPER.3
GND: C2.2, C3.2, C4.2, C5.2, C6.2, C7.2, C8.2, C9.2, C10.2, C11.2, C12.2, C13.2, C14.2, C15.2, C16.2, C17.2, C18.2, C19.2, C20.2, C21.2, C22.2, C23.2, C24.2, C25.2, C26.2, C27.2, C28.2, C29.2, C30.2, C31.2, C32.2, C33.2, C34.2, C35.2, C36.2, C37.2, C38.2, C39.2, C40.2, C41.2, C42.2, C43.2, C44.2, C45.2, C46.2, C47.2, C48.2, C49.2, C50.2, C51.2, C52.2, C53.2, C54.2, C55.2, C56.2, C57.2, C58.2, C59.2, C60.2, C61.2, C62.2, C63.2, C64.2, C65.2, C66.2, C67.2, C133.-, C134.-, C135.-, C136.2, C137.2, C138.2, C139.2, C140.2, C141.-, J1.2, J1.3, JP1.11, JP1.29, JP2.11, JP2.29, JUMPER.1, R4.1, R7.2, SV1.2, SV1.4, SV1.6, SV1.8, SV1.10, SV1.12, SV1.14, SV1.16, SV1.18, SV1.20, SV1.22, SV1.24, SV1.26, SV1.28, SV1.30, SV1.32, SV2.2, SV2.4, SV2.6, SV2.8, SV2.10, SV2.12, SV2.14, SV2.16, SV2.18, SV2.20, SV2.22, SV2.24, SV2.26, SV2.28, SV2.30, SV2.32, SV3.2, SV3.4, SV3.6, SV3.8, SV3.10, SV3.12, SV3.14, SV3.16, SV3.18, SV3.20, SV3.22, SV3.24, SV3.26, SV3.28, SV3.30, SV3.32, SV4.2, SV4.4, SV4.6, SV4.8, SV4.10, SV4.12, SV4.14, SV4.16, SV4.18, SV4.20, SV4.22, SV4.24, SV4.26, SV4.28, SV4.30, SV4.32, U1.4 (GND), U2.4 (GND), U3.4 (GND), U4.4 (GND), U5.4 (GND), U6.4 (GND), U7.4 (GND), U8.4 (GND), U9.4 (GND), U10.4 (GND), U11.4 (GND), U12.4 (GND), U13.4 (GND), U14.4 (GND), U15.4 (GND), U16.4 (GND), U17.4 (GND), U18.4 (GND), U19.4 (GND), U20.4 (GND), U21.4 (GND), U22.4 (GND), U23.4 (GND), U24.4 (GND), U25.4 (GND), U26.4 (GND), U27.4 (GND), U28.4 (GND), U29.4 (GND), U30.4 (GND), U31.4 (GND), U32.4 (GND), U33.4 (GND), U34.4 (GND), U35.4 (GND), U36.4 (GND), U37.4 (GND), U38.4 (GND), U39.4 (GND), U40.4 (GND), U41.4 (GND), U42.4 (GND), U43.4 (GND), U44.4 (GND), U45.4 (GND), U46.4 (GND), U47.4 (GND), U48.4 (GND), U49.4 (GND), U50.4 (GND), U51.4 (GND), U52.4 (GND), U53.4 (GND), U54.4 (GND), U55.4 (GND), U56.4 (GND), U57.4 (GND), U58.4 (GND), U59.4 (GND), U60.4 (GND), U61.4 (GND), U62.4 (GND), U63.4 (GND), U64.4 (GND), U65.4 (GND), U66.7 (GND), U66.18 (GND), U66.21 (GND), U66.25 (AGND), U66.26 (TEST), X1.5, X2.2
ID: X1.4
IN0: JP1.3, U1.2 (IN)
IN1: JP1.5, U2.2 (IN)
IN2: JP1.7, U3.2 (IN)
IN3: JP1.9, U4.2 (IN)
IN4: JP1.13, U5.2 (IN)
IN5: JP1.15, U6.2 (IN)
IN6: JP1.17, U7.2 (IN)
IN7: JP1.19, U8.2 (IN)
IN8: JP1.21, U9.2 (IN)
IN9: JP1.23, U10.2 (IN)
IN10: JP1.25, U11.2 (IN)
IN11: JP1.27, U12.2 (IN)
IN12: JP1.31, U13.2 (IN)
IN13: JP1.33, U14.2 (IN)
IN14: JP1.35, U15.2 (IN)
IN15: JP1.37, U16.2 (IN)
IN16: JP1.40, U17.2 (IN)
IN17: JP1.38, U18.2 (IN)
IN18: JP1.36, U19.2 (IN)
IN19: JP1.34, U20.2 (IN)
IN20: JP1.32, U21.2 (IN)
IN21: JP1.28, U22.2 (IN)
IN22: JP1.26, U23.2 (IN)
IN23: JP1.24, U24.2 (IN)
IN24: JP1.22, U25.2 (IN)
IN25: JP1.20, U26.2 (IN)
IN26: JP1.18, U27.2 (IN)
IN27: JP1.16, U28.2 (IN)
IN28: JP1.14, U29.2 (IN)
IN29: JP1.10, U30.2 (IN)
IN30: JP1.8, U31.2 (IN)
IN31: JP1.6, U32.2 (IN)
IN32: JP2.3, U33.2 (IN)
IN33: JP2.5, U34.2 (IN)
IN34: JP2.7, U35.2 (IN)
IN35: JP2.9, U36.2 (IN)
IN36: JP2.13, U37.2 (IN)
IN37: JP2.15, U38.2 (IN)
IN38: JP2.17, U39.2 (IN)
IN39: JP2.19, U40.2 (IN)
IN40: JP2.21, U41.2 (IN)
IN41: JP2.23, U42.2 (IN)
IN42: JP2.25, U43.2 (IN)
IN43: JP2.27, U44.2 (IN)
IN44: JP2.31, U45.2 (IN)
IN45: JP2.33, U46.2 (IN)
IN46: JP2.35, U47.2 (IN)
IN47: JP2.37, U48.2 (IN)
IN48: JP2.40, U49.2 (IN)
IN49: JP2.38, U50.2 (IN)
IN50: JP2.36, U51.2 (IN)
IN51: JP2.34, U52.2 (IN)
IN52: JP2.32, U53.2 (IN)
IN53: JP2.28, U54.2 (IN)
IN54: JP2.26, U55.2 (IN)
IN55: JP2.24, U56.2 (IN)
IN56: JP2.22, U57.2 (IN)
IN57: JP2.20, U58.2 (IN)
IN58: JP2.18, U59.2 (IN)
IN59: JP2.16, U60.2 (IN)
IN60: JP2.14, U61.2 (IN)
IN61: JP2.10, U62.2 (IN)
IN62: JP2.8, U63.2 (IN)
IN63: JP2.6, U64.2 (IN)
unnamed: JP1.12, R8.2
unnamed: D1.C, L2.A (1)
unnamed: D1.A, L1.C (2)
unnamed: R1.1, U65.5 (!SHDN!)
unnamed: R2.1, R3.2, U65.2 (UV)
unnamed: R3.1, R4.2, U65.3 (OV)
unnamed: T1.1 (S), T1.3 (S)
unnamed: T1.2 (G), T1.4 (G), U65.8 (GATE)
unnamed: LED1.C, R5.2
unnamed: LED2.C, R6.2
unnamed: C100.1, U33.5 (OUTL), U33.6 (OUTH)
unnamed: C101.1, U34.5 (OUTL), U34.6 (OUTH)
unnamed: C102.1, U35.5 (OUTL), U35.6 (OUTH)
unnamed: C103.1, U36.5 (OUTL), U36.6 (OUTH)
unnamed: C104.1, U37.5 (OUTL), U37.6 (OUTH)
unnamed: C105.1, U38.5 (OUTL), U38.6 (OUTH)
unnamed: C106.1, U39.5 (OUTL), U39.6 (OUTH)
unnamed: C107.1, U40.5 (OUTL), U40.6 (OUTH)
unnamed: C108.1, U41.5 (OUTL), U41.6 (OUTH)
unnamed: C109.1, U42.5 (OUTL), U42.6 (OUTH)
unnamed: C110.1, U43.5 (OUTL), U43.6 (OUTH)
unnamed: C111.1, U44.5 (OUTL), U44.6 (OUTH)
unnamed: C112.1, U45.5 (OUTL), U45.6 (OUTH)
unnamed: C113.1, U46.5 (OUTL), U46.6 (OUTH)
unnamed: C114.1, U47.5 (OUTL), U47.6 (OUTH)
unnamed: C115.1, U48.5 (OUTL), U48.6 (OUTH)
unnamed: C84.1, U17.5 (OUTL), U17.6 (OUTH)
unnamed: C85.1, U18.5 (OUTL), U18.6 (OUTH)
unnamed: C86.1, U19.5 (OUTL), U19.6 (OUTH)
unnamed: C87.1, U20.5 (OUTL), U20.6 (OUTH)
unnamed: C88.1, U21.5 (OUTL), U21.6 (OUTH)
unnamed: C89.1, U22.5 (OUTL), U22.6 (OUTH)
unnamed: C90.1, U23.5 (OUTL), U23.6 (OUTH)
unnamed: C91.1, U24.5 (OUTL), U24.6 (OUTH)
unnamed: C92.1, U25.5 (OUTL), U25.6 (OUTH)
unnamed: C93.1, U26.5 (OUTL), U26.6 (OUTH)
unnamed: C94.1, U27.5 (OUTL), U27.6 (OUTH)
unnamed: C95.1, U28.5 (OUTL), U28.6 (OUTH)
unnamed: C96.1, U29.5 (OUTL), U29.6 (OUTH)
unnamed: C97.1, U30.5 (OUTL), U30.6 (OUTH)
unnamed: C98.1, U31.5 (OUTL), U31.6 (OUTH)
unnamed: C99.1, U32.5 (OUTL), U32.6 (OUTH)
unnamed: C68.1, U1.5 (OUTL), U1.6 (OUTH)
unnamed: C69.1, U2.5 (OUTL), U2.6 (OUTH)
unnamed: C70.1, U3.5 (OUTL), U3.6 (OUTH)
unnamed: C71.1, U4.5 (OUTL), U4.6 (OUTH)
unnamed: C72.1, U5.5 (OUTL), U5.6 (OUTH)
unnamed: C73.1, U6.5 (OUTL), U6.6 (OUTH)
unnamed: C74.1, U7.5 (OUTL), U7.6 (OUTH)
unnamed: C75.1, U8.5 (OUTL), U8.6 (OUTH)
unnamed: C76.1, U9.5 (OUTL), U9.6 (OUTH)
unnamed: C77.1, U10.5 (OUTL), U10.6 (OUTH)
unnamed: C78.1, U11.5 (OUTL), U11.6 (OUTH)
unnamed: C79.1, U12.5 (OUTL), U12.6 (OUTH)
unnamed: C80.1, U13.5 (OUTL), U13.6 (OUTH)
unnamed: C81.1, U14.5 (OUTL), U14.6 (OUTH)
unnamed: C82.1, U15.5 (OUTL), U15.6 (OUTH)
unnamed: C83.1, U16.5 (OUTL), U16.6 (OUTH)
unnamed: C116.1, U49.5 (OUTL), U49.6 (OUTH)
unnamed: C117.1, U50.5 (OUTL), U50.6 (OUTH)
unnamed: C118.1, U51.5 (OUTL), U51.6 (OUTH)
unnamed: C119.1, U52.5 (OUTL), U52.6 (OUTH)
unnamed: C120.1, U53.5 (OUTL), U53.6 (OUTH)
unnamed: C121.1, U54.5 (OUTL), U54.6 (OUTH)
unnamed: C122.1, U55.5 (OUTL), U55.6 (OUTH)
unnamed: C123.1, U56.5 (OUTL), U56.6 (OUTH)
unnamed: C124.1, U57.5 (OUTL), U57.6 (OUTH)
unnamed: C125.1, U58.5 (OUTL), U58.6 (OUTH)
unnamed: C126.1, U59.5 (OUTL), U59.6 (OUTH)
unnamed: C127.1, U60.5 (OUTL), U60.6 (OUTH)
unnamed: C128.1, U61.5 (OUTL), U61.6 (OUTH)
unnamed: C129.1, U62.5 (OUTL), U62.6 (OUTH)
unnamed: C1130.1, U63.5 (OUTL), U63.6 (OUTH)
unnamed: C1131.1, U64.5 (OUTL), U64.6 (OUTH)
OSCI: C140.1, Q1.1, U66.27 (OSCI)
OSCO: C139.1, Q1.2, U66.28 (OSCO)
OUT0: C68.2, SV1.1
OUT1: C69.2, SV1.3
OUT2: C70.2, SV1.5
OUT3: C71.2, SV1.7
OUT4: C72.2, SV1.9
OUT5: C73.2, SV1.11
OUT6: C74.2, SV1.13
OUT7: C75.2, SV1.15
OUT8: C76.2, SV1.17
OUT9: C77.2, SV1.19
OUT10: C78.2, SV1.21
OUT11: C79.2, SV1.23
OUT12: C80.2, SV1.25
OUT13: C81.2, SV1.27
OUT14: C82.2, SV1.29
OUT15: C83.2, SV1.31
OUT16: C84.2, SV2.1
OUT17: C85.2, SV2.3
OUT18: C86.2, SV2.5
OUT19: C87.2, SV2.7
OUT20: C88.2, SV2.9
OUT21: C89.2, SV2.11
OUT22: C90.2, SV2.13
OUT23: C91.2, SV2.15
OUT24: C92.2, SV2.17
OUT25: C93.2, SV2.19
OUT26: C94.2, SV2.21
OUT27: C95.2, SV2.23
OUT28: C96.2, SV2.25
OUT29: C97.2, SV2.27
OUT30: C98.2, SV2.29
OUT31: C99.2, SV2.31
OUT32: C100.2, SV3.1
OUT33: C101.2, SV3.3
OUT34: C102.2, SV3.5
OUT35: C103.2, SV3.7
OUT36: C104.2, SV3.9
OUT37: C105.2, SV3.11
OUT38: C106.2, SV3.13
OUT39: C107.2, SV3.15
OUT40: C108.2, SV3.17
OUT41: C109.2, SV3.19
OUT42: C110.2, SV3.21
OUT43: C111.2, SV3.23
OUT44: C112.2, SV3.25
OUT45: C113.2, SV3.27
OUT46: C114.2, SV3.29
OUT47: C115.2, SV3.31
OUT48: C116.2, SV4.1
OUT49: C117.2, SV4.3
OUT50: C118.2, SV4.5
OUT51: C119.2, SV4.7
OUT52: C120.2, SV4.9
OUT53: C121.2, SV4.11
OUT54: C122.2, SV4.13
OUT55: C123.2, SV4.15
OUT56: C124.2, SV4.17
OUT57: C125.2, SV4.19
OUT58: C126.2, SV4.21
OUT59: C127.2, SV4.23
OUT60: C128.2, SV4.25
OUT61: C129.2, SV4.27
OUT62: C1130.2, SV4.29
OUT63: C1131.2, SV4.31
RX: JP1.1, U66.5 (RXD)
TX: JP1.2, U66.1 (TXD)
TXDEN: U66.13 (CBUS2)
VBUS: C138.1, L1.A (1), R8.1, X1.1
VCC: C137.1, C141.+, L2.C (2), U66.20 (VCC)
VDD: C2.1, C3.1, C4.1, C5.1, C6.1, C7.1, C8.1, C9.1, C10.1, C11.1, C12.1, C13.1, C14.1, C15.1, C16.1, C17.1, C18.1, C19.1, C20.1, C21.1, C22.1, C23.1, C24.1, C25.1, C26.1, C27.1, C28.1, C29.1, C30.1, C31.1, C32.1, C33.1, C34.1, C35.1, C36.1, C37.1, C38.1, C39.1, C40.1, C41.1, C42.1, C43.1, C44.1, C45.1, C46.1, C47.1, C48.1, C49.1, C50.1, C51.1, C52.1, C53.1, C54.1, C55.1, C56.1, C57.1, C58.1, C59.1, C60.1, C61.1, C62.1, C63.1, C64.1, C65.1, C66.1, C67.1, C133.+, C134.+, C135.+, T1.5 (D), T1.6 (D), U1.3 (VDD), U2.3 (VDD), U3.3 (VDD), U4.3 (VDD), U5.3 (VDD), U6.3 (VDD), U7.3 (VDD), U8.3 (VDD), U9.3 (VDD), U10.3 (VDD), U11.3 (VDD), U12.3 (VDD), U13.3 (VDD), U14.3 (VDD), U15.3 (VDD), U16.3 (VDD), U17.3 (VDD), U18.3 (VDD), U19.3 (VDD), U20.3 (VDD), U21.3 (VDD), U22.3 (VDD), U23.3 (VDD), U24.3 (VDD), U25.3 (VDD), U26.3 (VDD), U27.3 (VDD), U28.3 (VDD), U29.3 (VDD), U30.3 (VDD), U31.3 (VDD), U32.3 (VDD), U33.3 (VDD), U34.3 (VDD), U35.3 (VDD), U36.3 (VDD), U37.3 (VDD), U38.3 (VDD), U39.3 (VDD), U40.3 (VDD), U41.3 (VDD), U42.3 (VDD), U43.3 (VDD), U44.3 (VDD), U45.3 (VDD), U46.3 (VDD), U47.3 (VDD), U48.3 (VDD), U49.3 (VDD), U50.3 (VDD), U51.3 (VDD), U52.3 (VDD), U53.3 (VDD), U54.3 (VDD), U55.3 (VDD), U56.3 (VDD), U57.3 (VDD), U58.3 (VDD), U59.3 (VDD), U60.3 (VDD), U61.3 (VDD), U62.3 (VDD), U63.3 (VDD), U64.3 (VDD), U65.7 (VOUT)
VIN: J1.1, R1.2, R2.2, T1.7 (D), T1.8 (D), U65.1 (VIN)

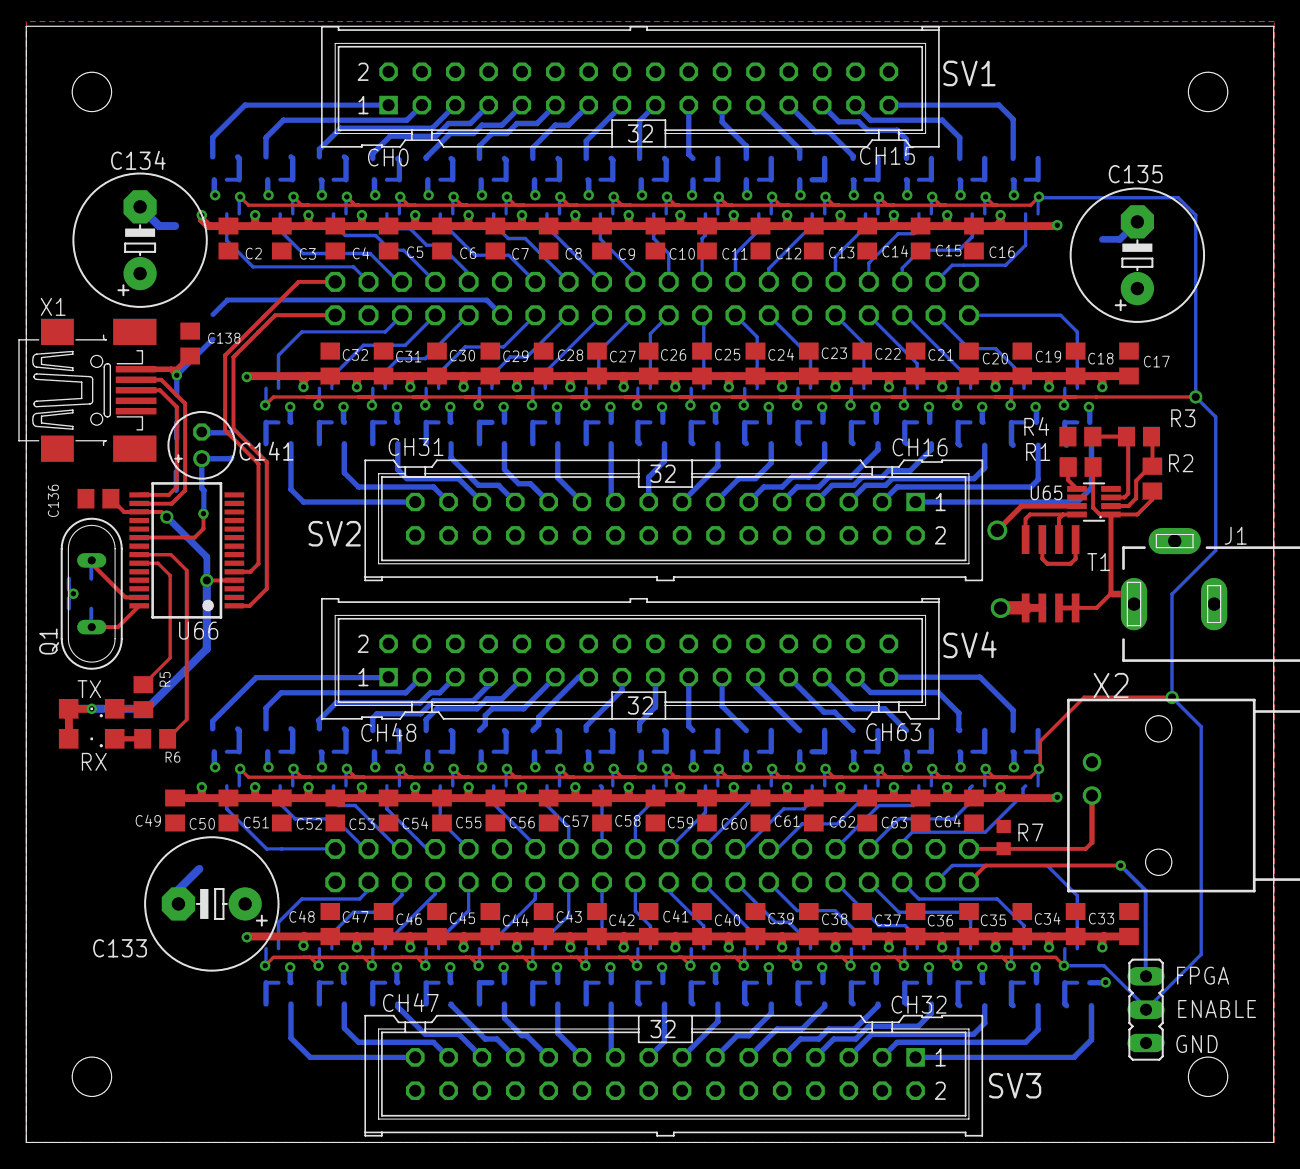
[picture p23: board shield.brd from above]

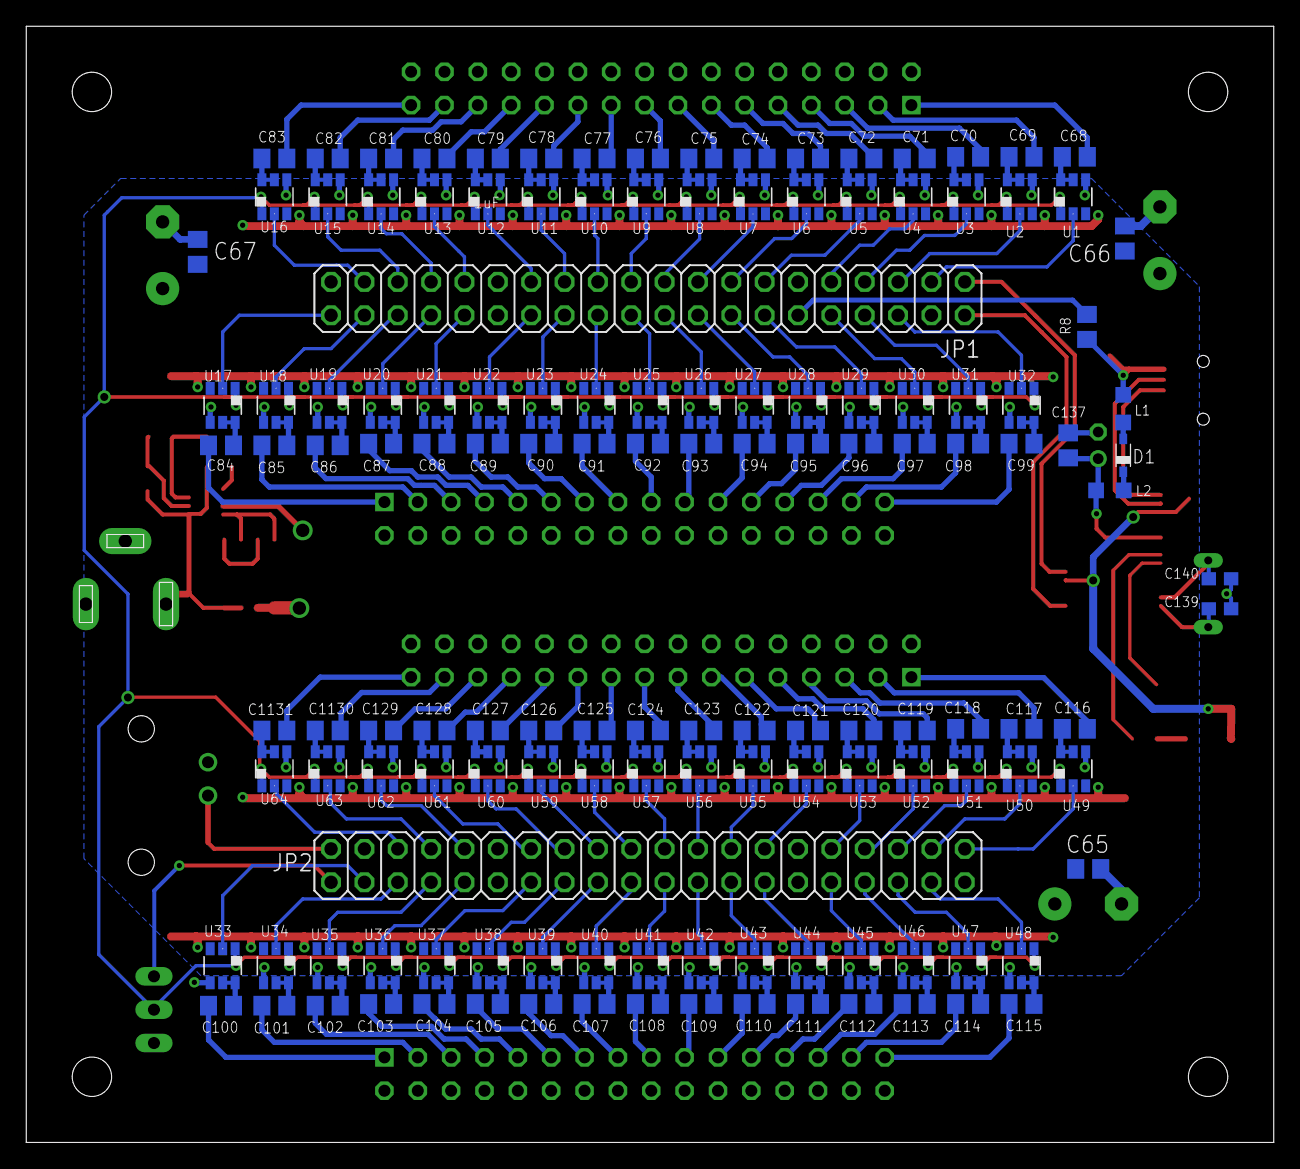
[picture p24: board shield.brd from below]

Board: 2 copper layers, 95.0 x 85.0 mm, 230 parts (140 on the bottom side), 219 nets.

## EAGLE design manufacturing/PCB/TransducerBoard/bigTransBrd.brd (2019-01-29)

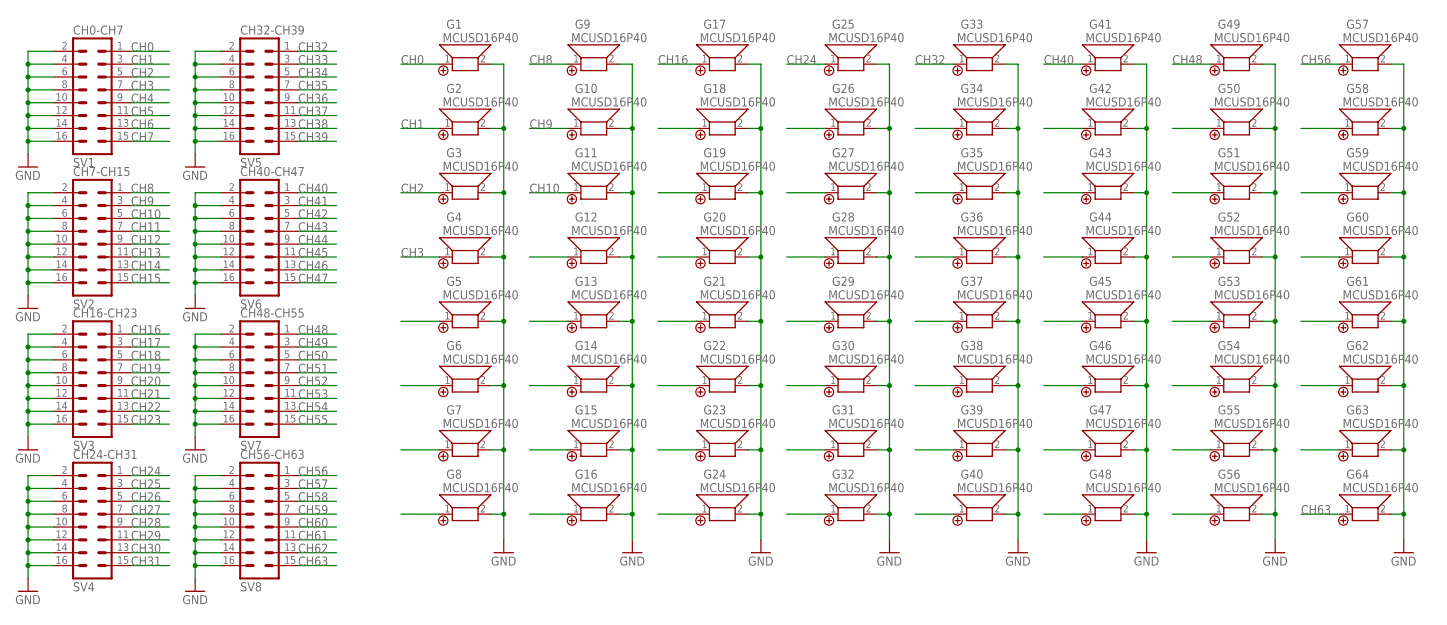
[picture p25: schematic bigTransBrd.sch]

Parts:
G1, G2, G3, G4, G5, G6, G7, G8, G9, G10, G11, G12, G13, G14, G15, G16, G17, G18, G19, G20, G21, G22, G23, G24, G25, G26, G27, G28, G29, G30, G31, G32, G33, G34, G35, G36, G37, G38, G39, G40, G41, G42, G43, G44, G45, G46, G47, G48, G49, G50, G51, G52, G53, G54, G55, G56, G57, G58, G59, G60, G61, G62, G63, G64: MCUSD16P40; D16P40
SV1: CH0-CH7; ML16
SV2: CH7-CH15; ML16
SV3: CH16-CH23; ML16
SV4: CH24-CH31; ML16
SV5: CH32-CH39; ML16
SV6: CH40-CH47; ML16
SV7: CH48-CH55; ML16
SV8: CH56-CH63; ML16

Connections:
CH0: G1.1, SV1.1
CH1: G2.1, SV1.3
CH2: G3.1, SV1.5
CH3: G4.1, SV1.7
CH4: G5.1, SV1.9
CH5: G6.1, SV1.11
CH6: G7.1, SV1.13
CH7: G8.1, SV1.15
CH8: G9.1, SV2.1
CH9: G10.1, SV2.3
CH10: G11.1, SV2.5
CH11: G12.1, SV2.7
CH12: G13.1, SV2.9
CH13: G14.1, SV2.11
CH14: G15.1, SV2.13
CH15: G16.1, SV2.15
CH16: G17.1, SV3.1
CH17: G18.1, SV3.3
CH18: G19.1, SV3.5
CH19: G20.1, SV3.7
CH20: G21.1, SV3.9
CH21: G22.1, SV3.11
CH22: G23.1, SV3.13
CH23: G24.1, SV3.15
CH24: G25.1, SV4.1
CH25: G26.1, SV4.3
CH26: G27.1, SV4.5
CH27: G28.1, SV4.7
CH28: G29.1, SV4.9
CH29: G30.1, SV4.11
CH30: G31.1, SV4.13
CH31: G32.1, SV4.15
CH32: G33.1, SV5.1
CH33: G34.1, SV5.3
CH34: G35.1, SV5.5
CH35: G36.1, SV5.7
CH36: G37.1, SV5.9
CH37: G38.1, SV5.11
CH38: G39.1, SV5.13
CH39: G40.1, SV5.15
CH40: G41.1, SV6.1
CH41: G42.1, SV6.3
CH42: G43.1, SV6.5
CH43: G44.1, SV6.7
CH44: G45.1, SV6.9
CH45: G46.1, SV6.11
CH46: G47.1, SV6.13
CH47: G48.1, SV6.15
CH48: G49.1, SV7.1
CH49: G50.1, SV7.3
CH50: G51.1, SV7.5
CH51: G52.1, SV7.7
CH52: G53.1, SV7.9
CH53: G54.1, SV7.11
CH54: G55.1, SV7.13
CH55: G56.1, SV7.15
CH56: G57.1, SV8.1
CH57: G58.1, SV8.3
CH58: G59.1, SV8.5
CH59: G60.1, SV8.7
CH60: G61.1, SV8.9
CH61: G62.1, SV8.11
CH62: G63.1, SV8.13
CH63: G64.1, SV8.15
GND: G1.2, G2.2, G3.2, G4.2, G5.2, G6.2, G7.2, G8.2, G9.2, G10.2, G11.2, G12.2, G13.2, G14.2, G15.2, G16.2, G17.2, G18.2, G19.2, G20.2, G21.2, G22.2, G23.2, G24.2, G25.2, G26.2, G27.2, G28.2, G29.2, G30.2, G31.2, G32.2, G33.2, G34.2, G35.2, G36.2, G37.2, G38.2, G39.2, G40.2, G41.2, G42.2, G43.2, G44.2, G45.2, G46.2, G47.2, G48.2, G49.2, G50.2, G51.2, G52.2, G53.2, G54.2, G55.2, G56.2, G57.2, G58.2, G59.2, G60.2, G61.2, G62.2, G63.2, G64.2, SV1.2, SV1.4, SV1.6, SV1.8, SV1.10, SV1.12, SV1.14, SV1.16, SV2.2, SV2.4, SV2.6, SV2.8, SV2.10, SV2.12, SV2.14, SV2.16, SV3.2, SV3.4, SV3.6, SV3.8, SV3.10, SV3.12, SV3.14, SV3.16, SV4.2, SV4.4, SV4.6, SV4.8, SV4.10, SV4.12, SV4.14, SV4.16, SV5.2, SV5.4, SV5.6, SV5.8, SV5.10, SV5.12, SV5.14, SV5.16, SV6.2, SV6.4, SV6.6, SV6.8, SV6.10, SV6.12, SV6.14, SV6.16, SV7.2, SV7.4, SV7.6, SV7.8, SV7.10, SV7.12, SV7.14, SV7.16, SV8.2, SV8.4, SV8.6, SV8.8, SV8.10, SV8.12, SV8.14, SV8.16

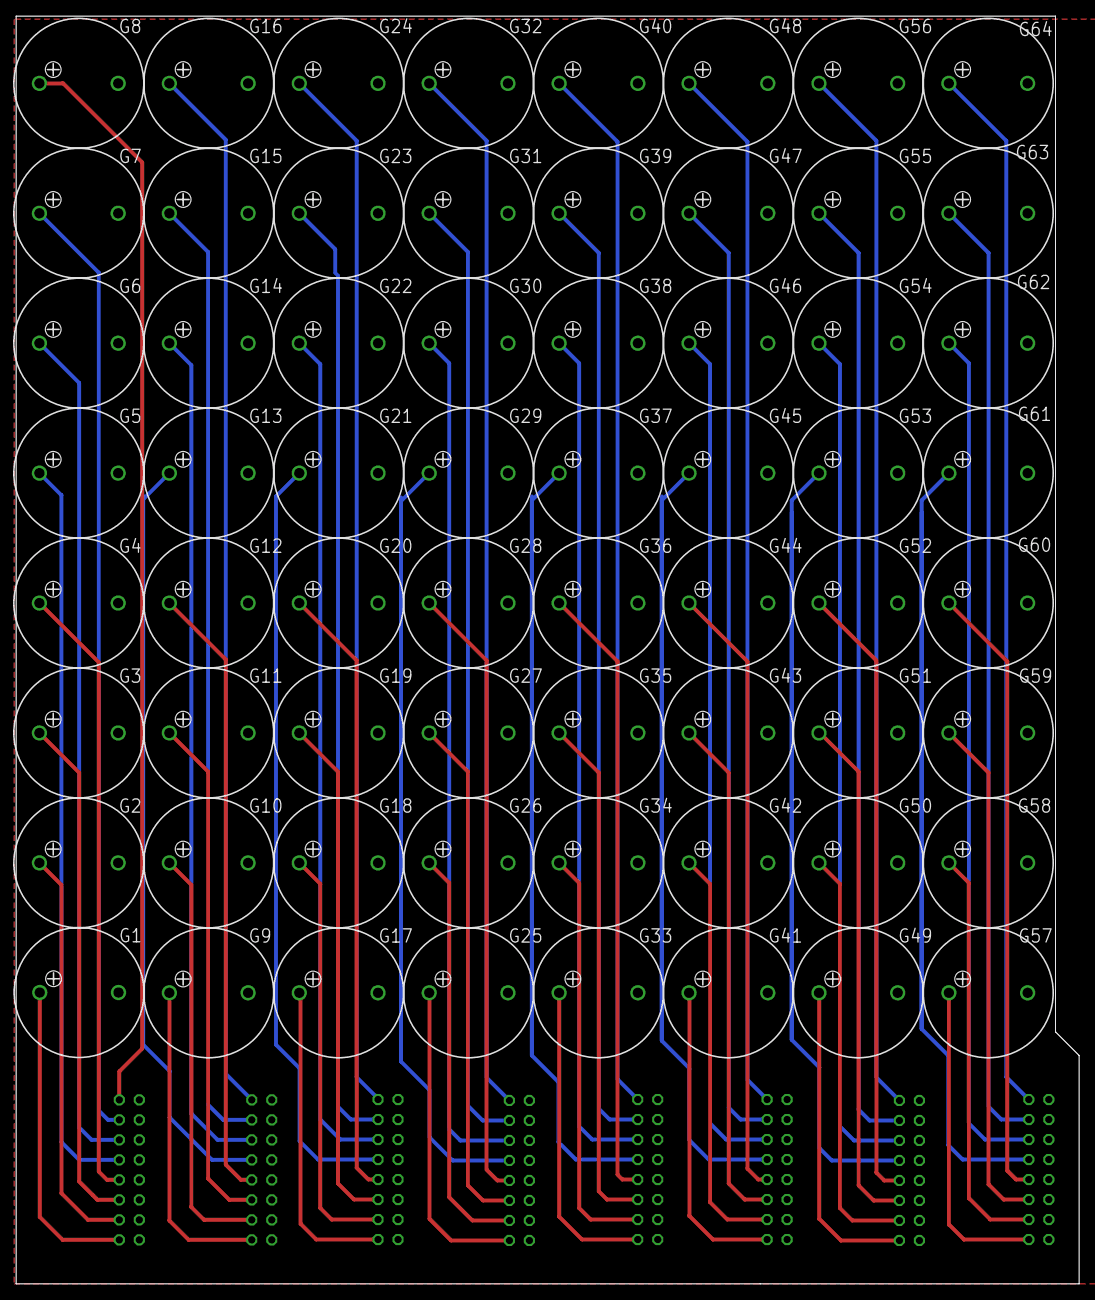
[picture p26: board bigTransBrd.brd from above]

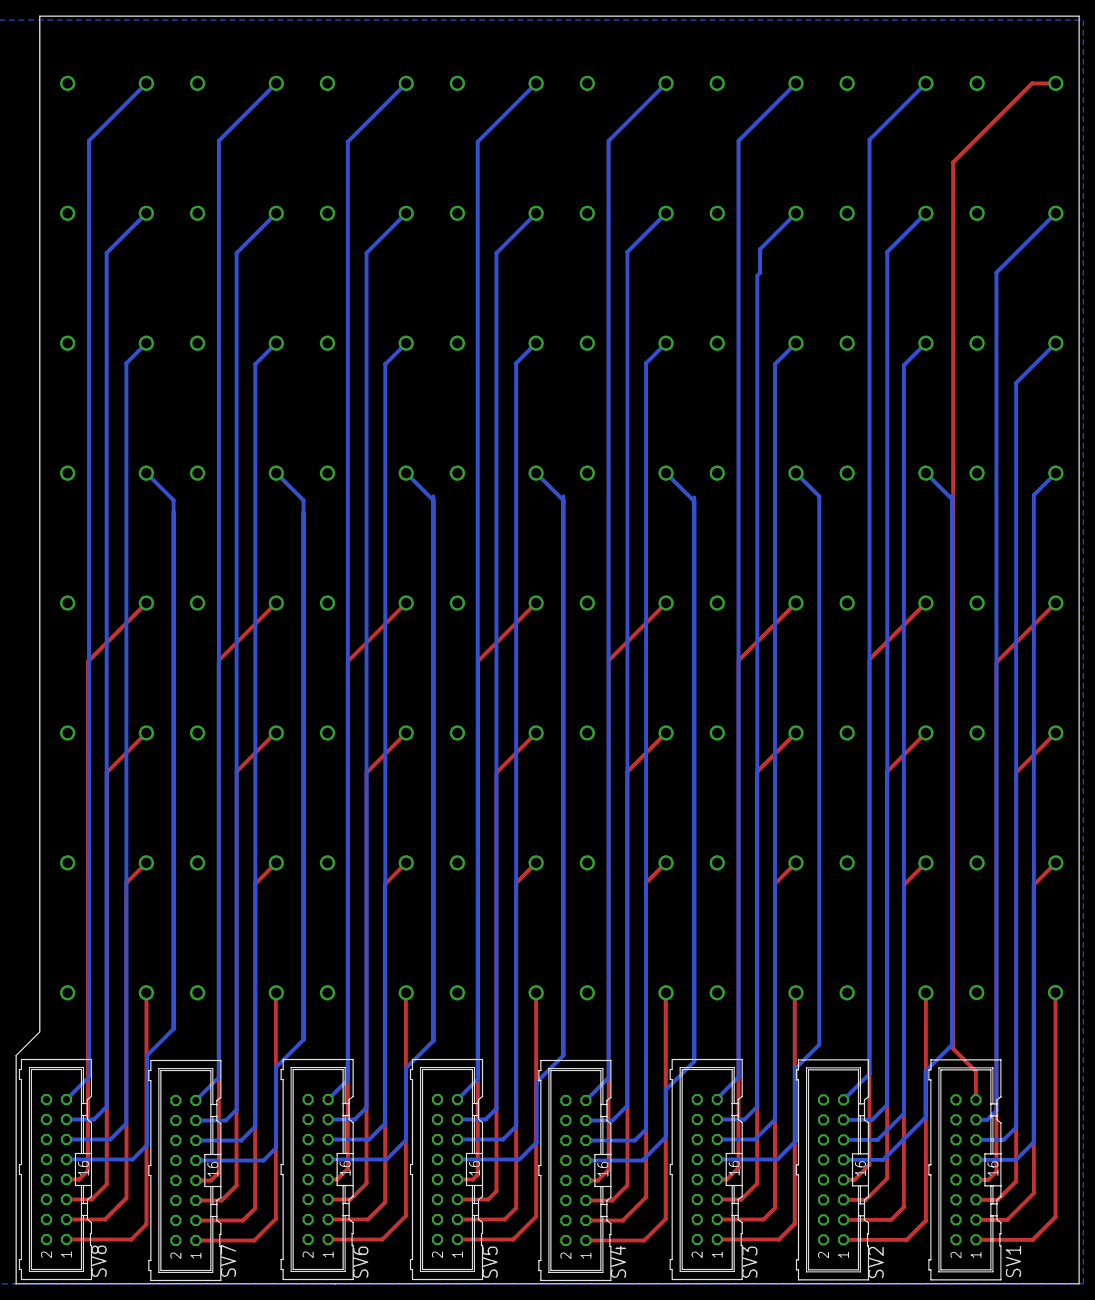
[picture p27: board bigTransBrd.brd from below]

Board: 2 copper layers, 135.0 x 161.0 mm, 72 parts (8 on the bottom side), 65 nets.

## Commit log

2019-02-20 converted SVG drawings to DXF
    [bigTransducerBox.dxf, bottomPanel.dxf, middlePanel.dxf, transducerBox.dxf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]
2019-03-04 added text to middle panel, added shield
    [shield.dxf]
2019-03-04 created documentation on assembly
2019-05-30 modified pin assignments to work with Shield v1.1
2019-05-30 fixed RX/TX swap, added power from USB option (Shield v1.1 ready for production)
    [shield.brd, shield.sch]
